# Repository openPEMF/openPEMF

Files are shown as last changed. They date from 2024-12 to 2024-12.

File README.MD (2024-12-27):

# <openPEMF>

## Description

Open source PEMF project that includes the hardware and firmware for anyone looking to build their own PEMF device

- Aren't there already some open source PEMF projects?  
    Yes, but many of them do not create the same fields used in the majority of published PEMF parameters. Most of them also have switching characteristics that cause spurious spike and oscillations that could be considered "dirty electricity"

- Why share this project?  
    Because PEMF with the right parameters has the ability to change peoples lives. From regenerating cartilage to reducing inflammation, many people get out of pain they have had for years. Something this powerful should not be stuck behind high price tags.

- What problem does it solve?  
    PEMF devices with good parameters cost a lot, cheap PEMF devices do not create magnetic fields that use the parameters used in the majority of PEMF studies

This open source PEMF project provides all the files necessary to make your own PEMF device that can be used to re-create the majority of PEMF parameters used in the majority of published PEMF studies.

PEMF has been proven to do lots of amazing things including regenerate cartilage and decrease inflammation, but don't take our word for it, go read some of the published studies and take a look at the science yourself!

The project allows you to tune your own magnetic field intensity and slew rate. This can be accomplished by either changing the voltage from the power supply, or by changing the pulse width.

Reach out with any questions or suggestions! Lets build this together and create a future where all people can access PEMF and benefit from the improved quality of life!
You can reach us at openpemf@gmail.com

## Table of Contents

- [How To Build](#How-to-build)
- [Usage](#usage)
- [Features](#features)

## How to build

The Gerber files, BOM and .POS files are already for purchase at JLCPCB.com. You should be able to upload these to JLCPCB and order complete (or mostly complete - depending on part availability) PCBs ready to run!

Once you have your PCBs, the first thing that you will want to do is upload the arduino code. The file "TEST.ino" is set up to run at 10hz and if you don't want to make any changes you can simply upload this file using the Arduino IDE. You will need to install the Raspberry Pi Pico board definitions since this design uses an RP2040 as it's processor. If you want to re-upload code, there are 2 holes in the pcb that you can bridge with a paperclip to get it into bootloader mode.

If you are not familiar with arduino or PCB ordering we can send out a kit. Email us at openpemf@gmail.com.

This board is designed to fit in this enclosure:
https://www.ebay.com/itm/266629727778?mkcid=16&mkevt=1&mkrid=711-127632-2357-0&ssspo=g7l9ZZJUQN-&sssrc=2047675&ssuid=7-kgmmceqts&widget_ver=artemis&media=COPY

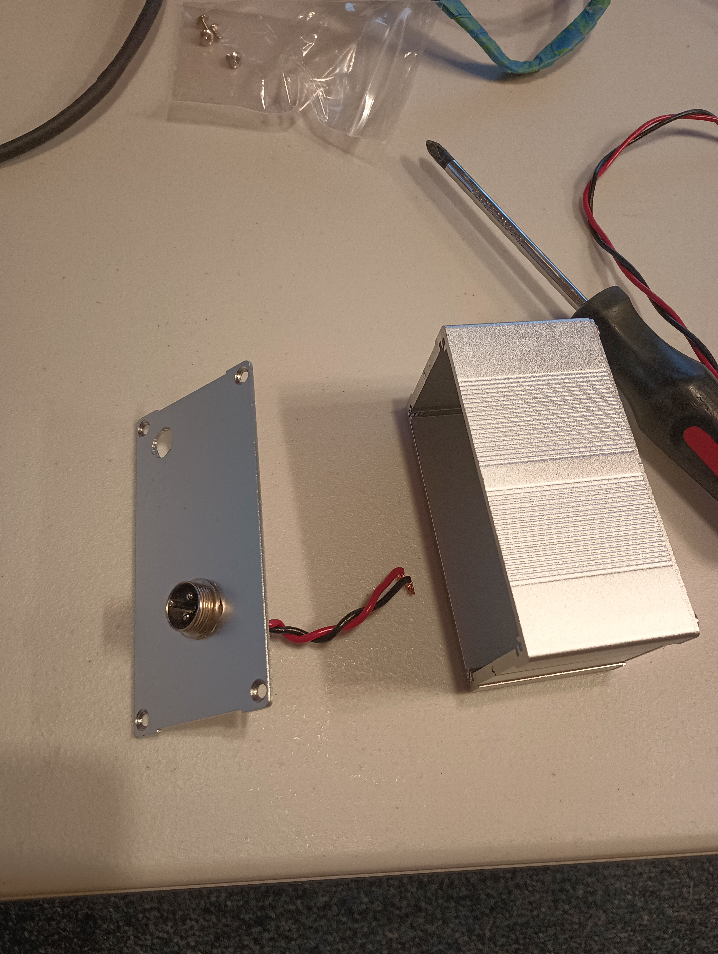
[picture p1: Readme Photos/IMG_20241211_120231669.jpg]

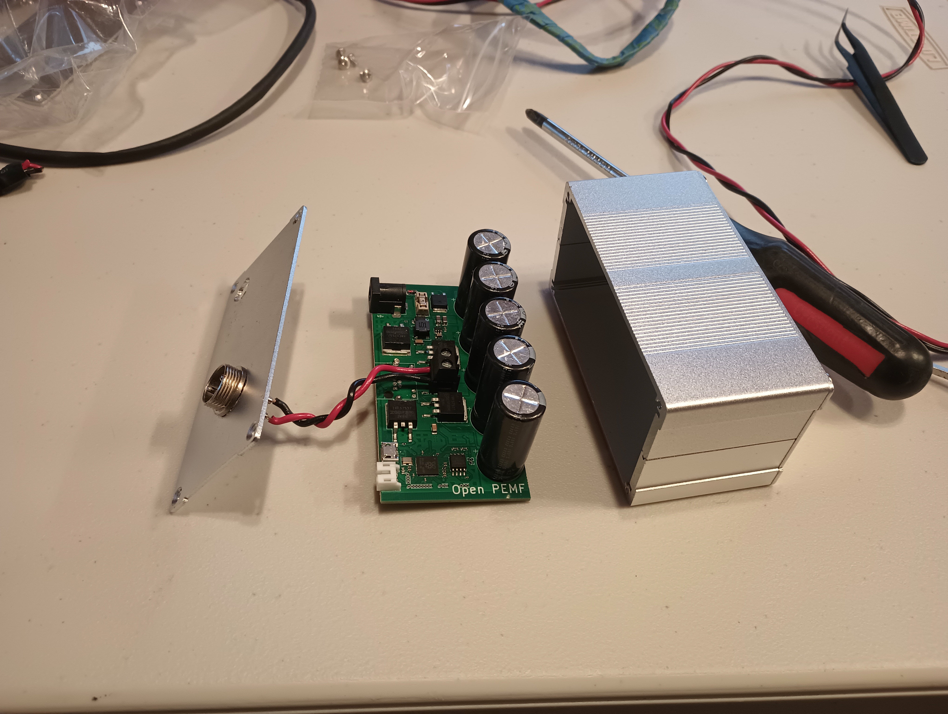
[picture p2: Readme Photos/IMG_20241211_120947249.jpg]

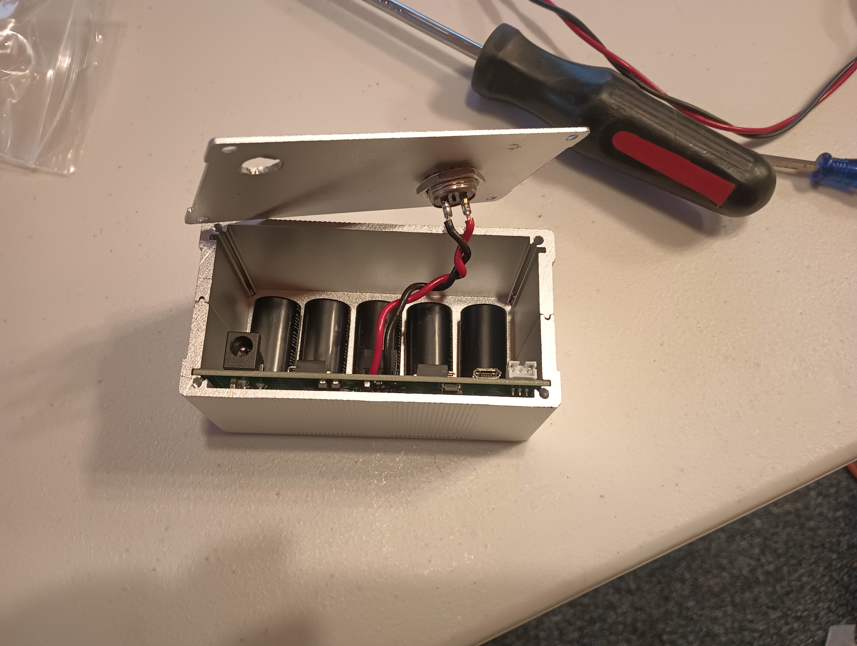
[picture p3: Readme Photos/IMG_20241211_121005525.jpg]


You can see that we used a simple circular connector to get the PEMF power through the enclosure. Ideally a 4 pin connector would be used for larger coils/currents. A handheld drill is an okay option to add the holes. Another option would be something 3D printed or laser cut. Please contribute these if you end up making them!

The coil should be wound from some form of wire. The closer the wires are together, the more efficient the coil will be. Using regular insulated wire still works well, but you will get more magnetic field from using enameled magnet wire.

Here is what our prototype coil looked like:
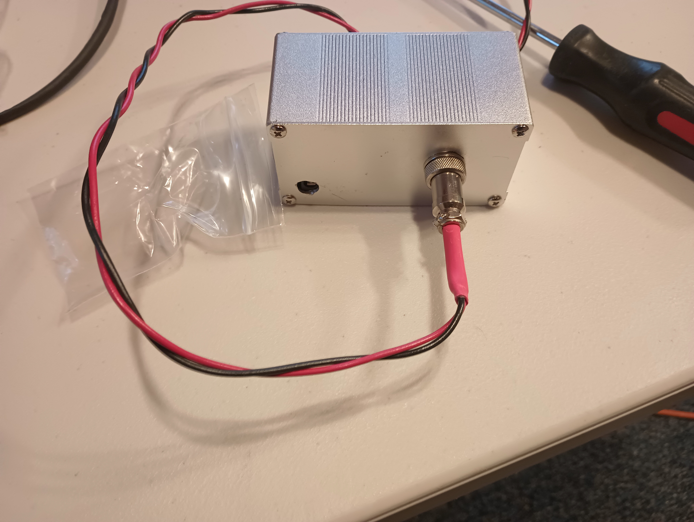
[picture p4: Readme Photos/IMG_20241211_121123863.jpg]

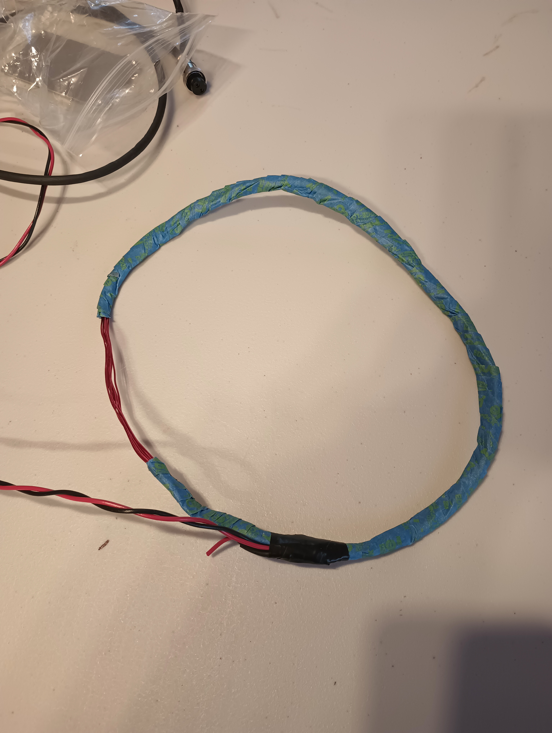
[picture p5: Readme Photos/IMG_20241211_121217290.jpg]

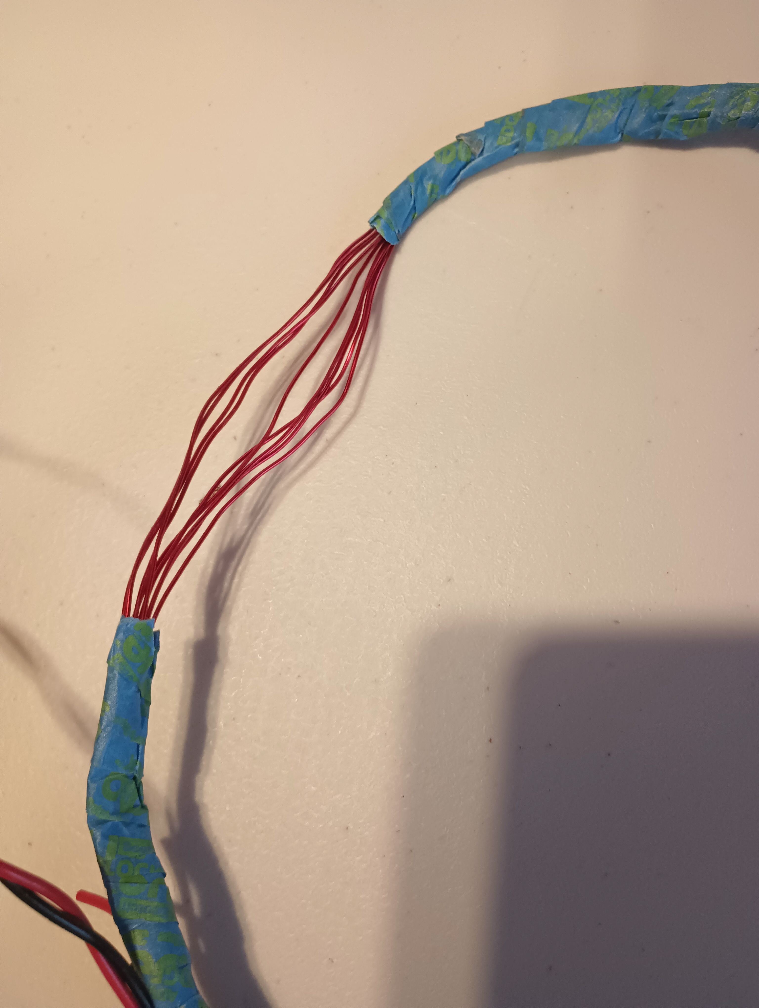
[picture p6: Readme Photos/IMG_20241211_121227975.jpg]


This sensor is great to see what the fields look like around your coil. Simply give it power and connect it to an oscilloscope:
https://www.digikey.com/en/products/detail/asahi-kasei-microdevices-akm/EQ733L/5822654

The coil we made had around 3 mT at the center, and around 10 mT close to the wires.

You will want a power supply that can run the board well. We found that this one worked well:
https://www.digikey.com/en/products/detail/fsp-technology-inc/FSP040-DWAN3/15713237 

## Usage
Simply place the loop over any part of your body that needs improvement. We like to look up published studies to see how long to use the PEMF for. You can even wind coils that are smaller with higher intensity or larger for a larger magnetic field.

## Features

There are a lot of features to OpenPEMF! Here are a few:
* Mosfet gate slew is limited -  this prevents parasitic turn on during the falling side of the signal
* There is an RC snubber across the h-bridge, removing certain oscillations that are not wanted
* Bi-polar pulses
* Programmable frequencies

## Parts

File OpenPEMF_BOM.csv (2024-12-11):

Reference | Value | Footprint | Field5
C1,C4,C5,C11,C12,C14,C34,C39,C40 | 1n_250V | Capacitor_SMD:C_1206_3216Metric | C915351
C2,C3,C15,C16,C17,C18,C19,C20,C21,C22,C23,C24,C25,C35,C36,C41,C42 | 100n | Capacitor_SMD:C_0402_1005Metric | C307331
C6,C26,C28,C29,C43,C44 | 2.2u | Capacitor_SMD:C_1206_3216Metric | C577211
C7,C8,C9,C10,C13 | 470u_100V | Capacitor_THT:CP_Radial_D16.0mm_P7.50mm | C340709
C27,C30,C31,C32,C37,C38 | 4.7u | Capacitor_SMD:C_1206_3216Metric | C29823
C33 | 100n | Capacitor_SMD:C_0805_2012Metric | C28233
C45,C46 | 36pf | Capacitor_SMD:C_0402_1005Metric | C541436
D1,D2,D16,D17,D21,D22 | BAT46W-7-F | Diode_SMD:D_SOD-123 | C83152
D3,D4,D14,D15,D18,D19 | 5.6 | Diode_SMD:D_MiniMELF | C2982194
D5,D6,D7,D23 | D_AAK | Package_TO_SOT_SMD:TO-277A | C2693410
D8 | SMAJ54CA | Diode_SMD:D_SMA | C173507
D20 | D_Schottky | Diode_SMD:D_SMA | C14996
F1 | 0154005.DRT | Fuse:Fuseholder_Littelfuse_Nano2_154x | C206917
J2 | Screw_Terminal_01x02 | TerminalBlock_Phoenix:TerminalBlock_Phoenix_MKDS-1,5-2-5.08_1x02_P5.08mm_Horizontal | C430601
J3,J4,J5,J7,J9 | -- mixed values -- | -- mixed values --
J8 | USB_B_Micro | OpenPEMFfp:AMPHENOL_10118194-0001LF | C132563
J10 | Barrel_Jack_Switch | OpenPEMFfp:C319099 | C720558
L1 | 100u | Inductor_SMD:L_Coilcraft_XAL6060-XXX | C341070
Q1,Q2,Q3,Q4 | Q_NMOS_GDS | Package_TO_SOT_SMD:TO-263-2 | C538034
Q5 | Q_PMOS_GDS | Package_TO_SOT_SMD:TO-252-2 | C2585
R1,R2,R7,R8,R14,R18 | 1k | Resistor_SMD:R_0603_1608Metric | C21190
R3,R12,R13 | 150 | Resistor_SMD:R_0805_2012Metric | C17471
R4,R11,R25 | 100 | Resistor_SMD:R_0402_1005Metric | C25076
R5,R9,R15,R16 | 27.4 | Resistor_SMD:R_0402_1005Metric | C172043
R6,R10,R19,R23 | 100k | Capacitor_SMD:C_0603_1608Metric | C25803
R17,R21,R22 | 10k | Resistor_SMD:R_0603_1608Metric | C25804
R20 | 1Meg | Capacitor_SMD:C_0603_1608Metric | C22935
R24 | 6.8k | Resistor_SMD:R_0603_1608Metric | C23212
U2 | TL072 | Package_SO:SOIC-8_3.9x4.9mm_P1.27mm | C6961
U3,U5 | EL3H7BTA-VG | OpenPEMFfp:SOIC_BTA-VG_EVS | C32565
U6 | RP2040 | OpenPEMFfp:RP2040 | C2040
U7 | W25Q128JVS | Package_SO:SOIC-8_5.23x5.23mm_P1.27mm | C97521
U8 | AMS1117-3.3 | Package_TO_SOT_SMD:SOT-223-3_TabPin2 | C6186
U9 | LMR16006 | Package_TO_SOT_SMD:SOT-23-6 | C87080
U10 | NE555DR | Package_SO:SOIC-8_3.9x4.9mm_P1.27mm | C7593
Y1 | 12Mhz | Crystal:Crystal_SMD_3225-4Pin_3.2x2.5mm | C9002

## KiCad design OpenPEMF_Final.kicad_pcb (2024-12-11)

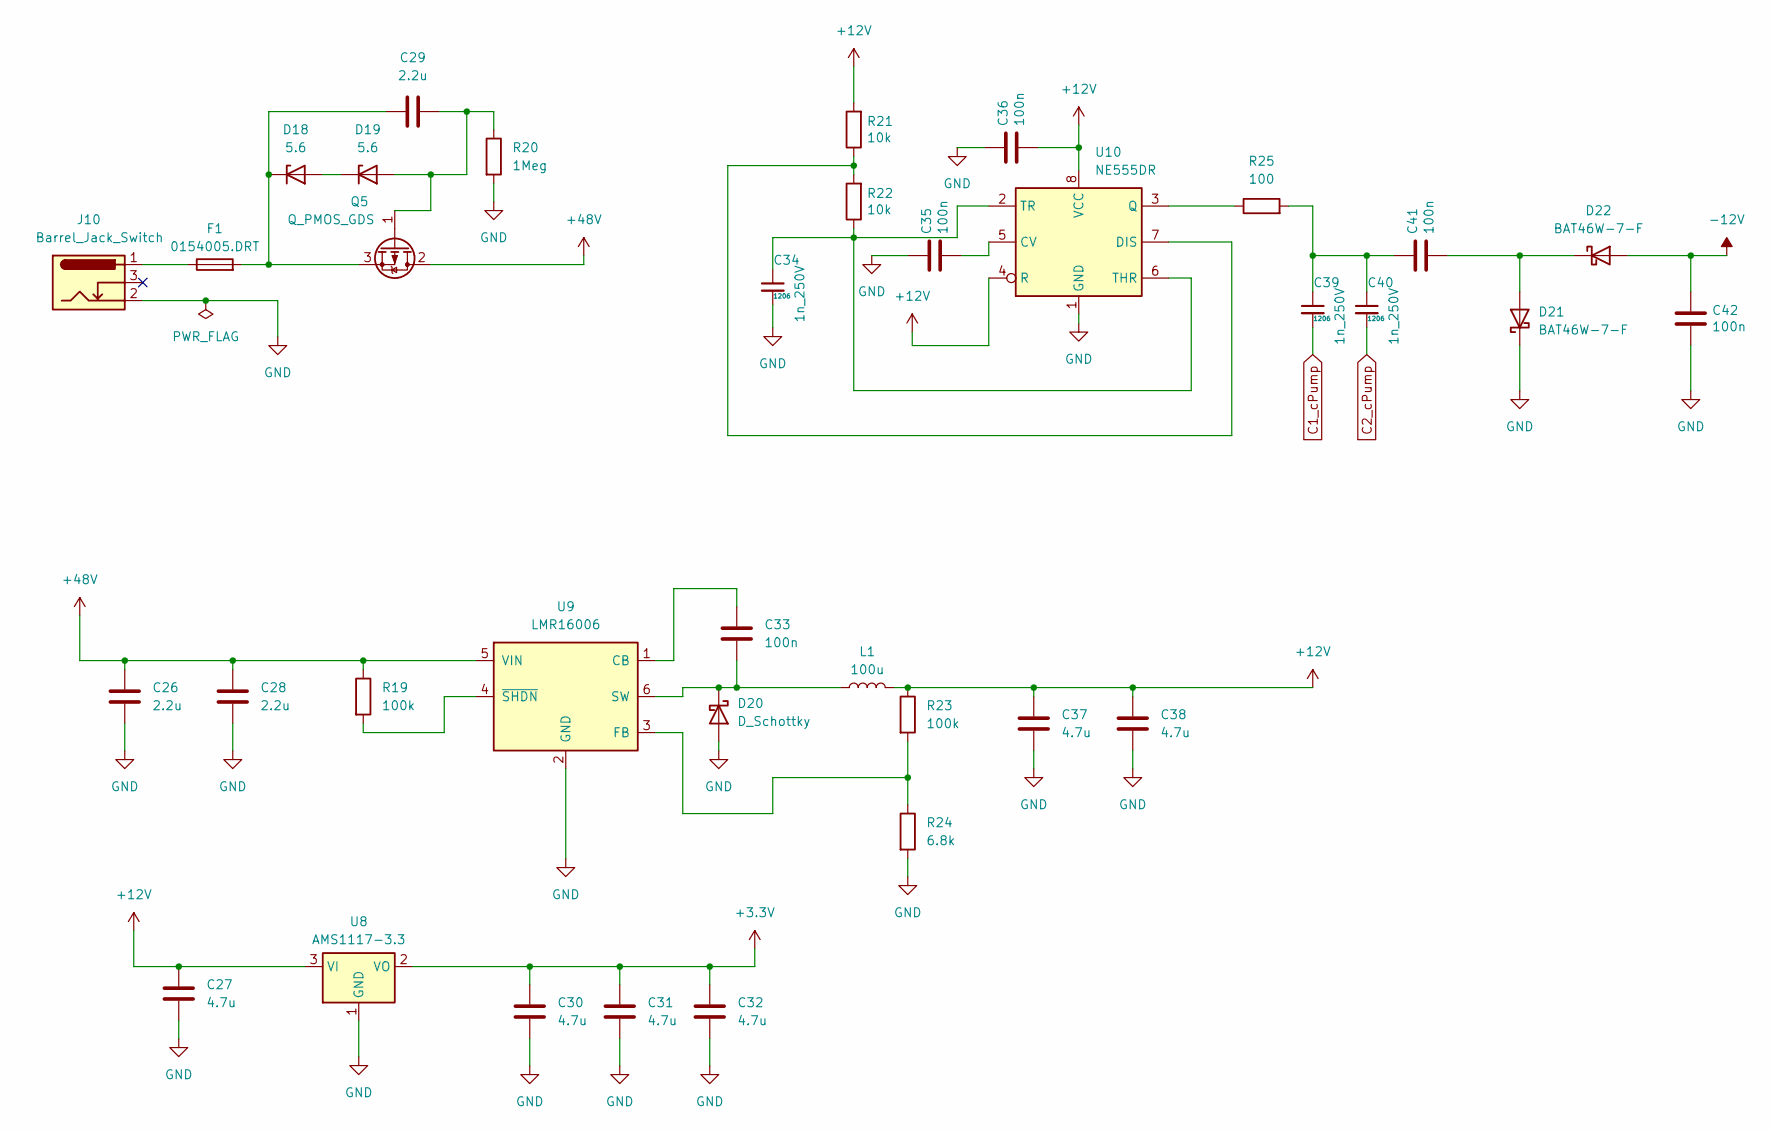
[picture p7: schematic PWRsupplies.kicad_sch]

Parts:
C26, C28, C29: 2.2u; C_1206_3216Metric
C27, C30, C31, C32, C37, C38: 4.7u; C_1206_3216Metric
C33: 100n; C_0805_2012Metric
C34, C39, C40: 1n_250V; C_1206_3216Metric
C35, C36, C41, C42: 100n; C_0402_1005Metric
D18, D19: 5.6; D_MiniMELF
D20: D_Schottky; D_SMA
D21, D22: BAT46W-7-F; D_SOD-123
F1: 0154005.DRT; Fuseholder_Littelfuse_Nano2_154x
J10: Barrel_Jack_Switch; C319099
L1: 100u; L_Coilcraft_XAL6060-XXX
Q5: Q_PMOS_GDS; TO-252-2
R19, R23: 100k; C_0603_1608Metric
R20: 1Meg; C_0603_1608Metric
R21, R22: 10k; R_0603_1608Metric
R24: 6.8k; R_0603_1608Metric
R25: 100; R_0402_1005Metric
U8: AMS1117-3.3; SOT-223-3_TabPin2
U9: LMR16006; SOT-23-6
U10: NE555DR; SOIC-8_3.9x4.9mm_P1.27mm

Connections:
+3.3V: C30.1, C31.1, C32.1, U8.2 (VO); also elsewhere on the board
+12V: C27.1, C36.2, C37.1, C38.1, L1.2, R21.2, R23.1, U8.3 (VI), U10.4 (R), U10.8 (VCC); also elsewhere on the board
+48V: C26.1, C28.1, Q5.2 (D), R19.1, U9.5 (VIN); also elsewhere on the board
-12V: C42.1, D22.2 (A); also elsewhere on the board
C1_cPump: C39.2; also elsewhere on the board
C2_cPump: C40.2; also elsewhere on the board
GND: C26.2, C27.2, C28.2, C30.2, C31.2, C32.2, C34.2, C35.1, C36.1, C37.2, C38.2, C42.2, D20.2 (A), D21.1 (K), J10.2, R20.2, R24.2, U8.1 (GND), U9.2 (GND), U10.1 (GND); also elsewhere on the board
unnamed: C39.1, C40.1, C41.1, R25.2
unnamed: D18.2 (A), D19.1 (K)
unnamed: C29.1, D18.1 (K), F1.2, Q5.3 (S)
unnamed: C29.2, D19.2 (A), Q5.1 (G), R20.1
unnamed: C33.2, D20.1 (K), L1.1, U9.6 (SW)
unnamed: C41.2, D21.2 (A), D22.1 (K)
unnamed: F1.1, J10.1
unnamed: C33.1, U9.1 (CB)
unnamed: R23.2, R24.1, U9.3 (FB)
unnamed: R19.2, U9.4 (~SHDN)
unnamed: C35.2, U10.5 (CV)
unnamed: R21.1, R22.2, U10.7 (DIS)
unnamed: R25.1, U10.3 (Q)
unnamed: C34.1, R22.1, U10.2 (TR), U10.6 (THR)

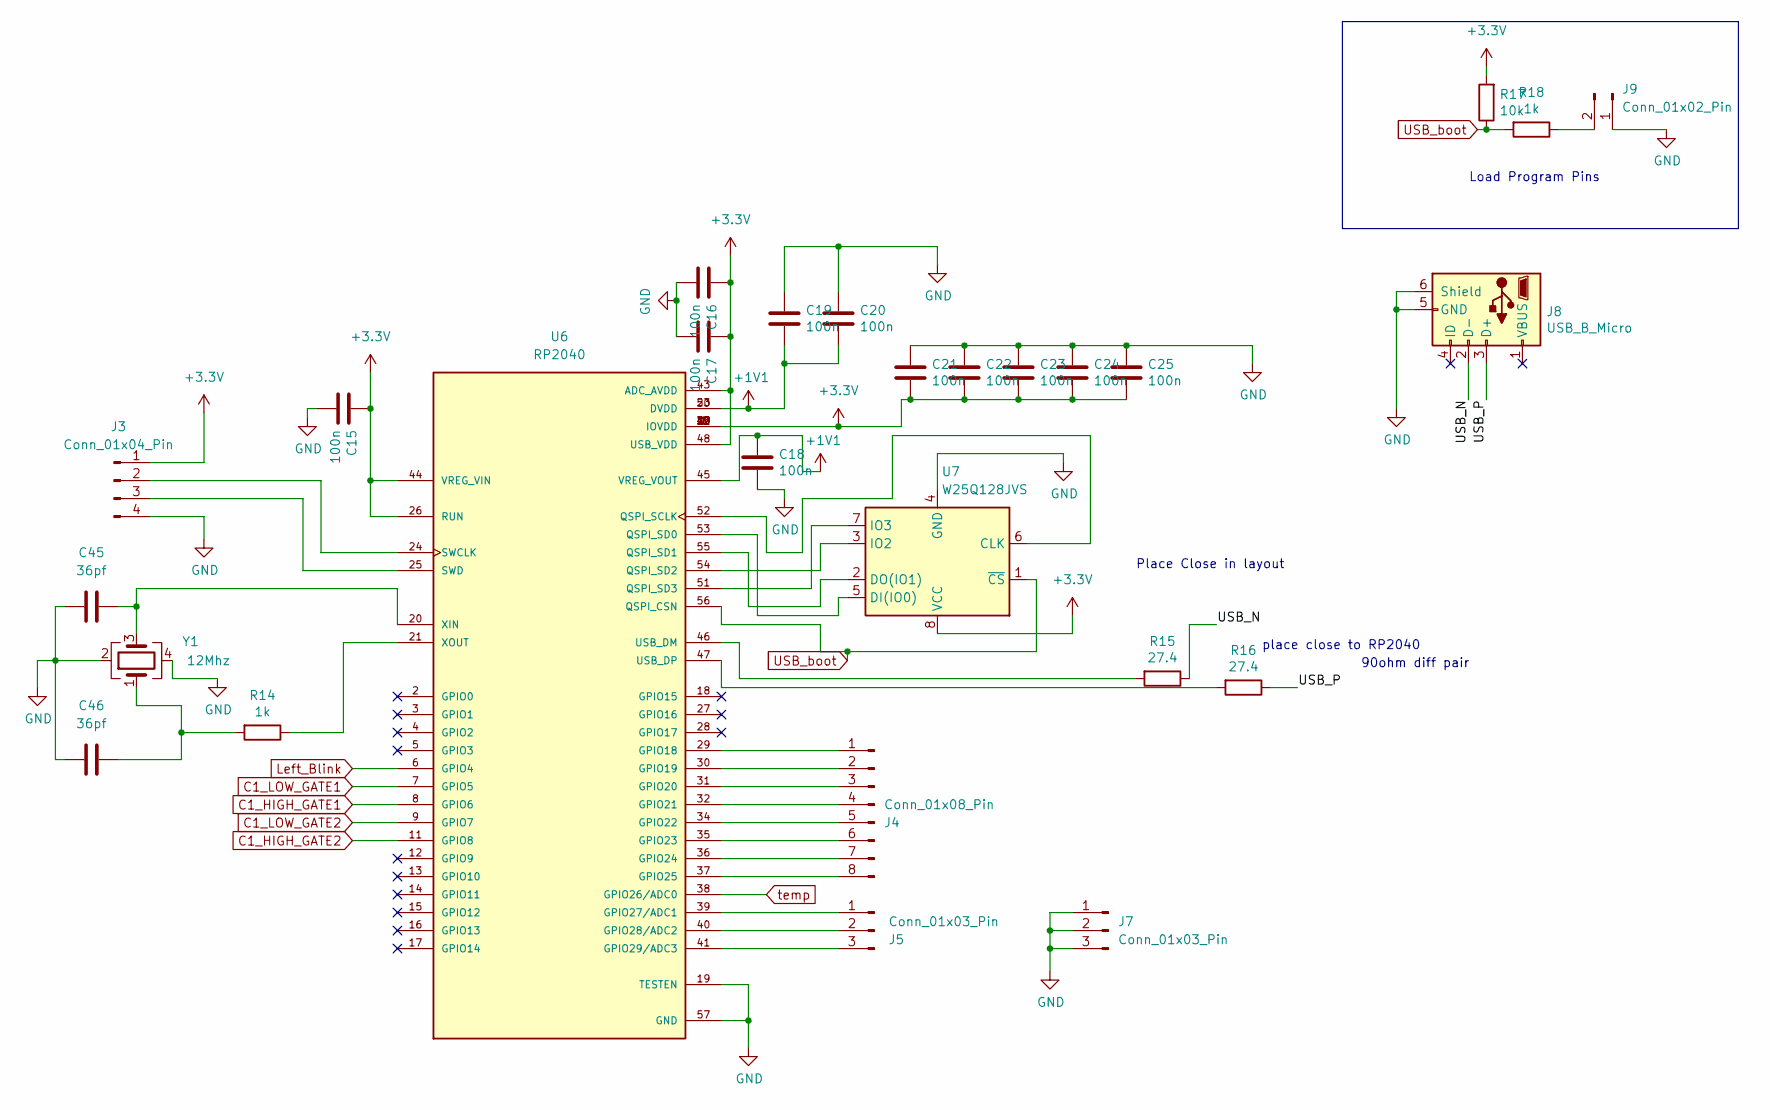
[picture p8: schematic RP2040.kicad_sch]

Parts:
C15, C16, C17, C18, C19, C20, C21, C22, C23, C24, C25: 100n; C_0402_1005Metric
C45, C46: 36pf; C_0402_1005Metric
J3: Conn_01x04_Pin; PinHeader_1x04_P1.00mm_Vertical
J4: Conn_01x08_Pin; PinHeader_1x08_P1.00mm_Vertical
J5, J7: Conn_01x03_Pin; PinHeader_1x03_P1.00mm_Vertical
J8: USB_B_Micro; AMPHENOL_10118194-0001LF
J9: Conn_01x02_Pin; PinHeader_1x02_P1.27mm_Vertical
R14, R18: 1k; R_0603_1608Metric
R15, R16: 27.4; R_0402_1005Metric
R17: 10k; R_0603_1608Metric
U6: RP2040; PARTREV 1.6.1
U7: W25Q128JVS; SOIC-8_5.23x5.23mm_P1.27mm
Y1: 12Mhz; Crystal_SMD_3225-4Pin_3.2x2.5mm

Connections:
+1V1: C18.1, C19.2, C20.2, U6.23 (DVDD), U6.45 (VREG_VOUT), U6.50 (DVDD)
+3.3V: C15.1, C16.1, C17.1, C21.2, C22.2, C23.2, C24.2, C25.2, J3.1, R17.2, U6.1 (IOVDD), U6.10 (IOVDD), U6.22 (IOVDD), U6.26 (RUN), U6.33 (IOVDD), U6.42 (IOVDD), U6.43 (ADC_AVDD), U6.44 (VREG_VIN), U6.48 (USB_VDD), U6.49 (IOVDD), U7.8 (VCC); also elsewhere on the board
/RP2040/USB_N: J8.2 (D-), R15.1
/RP2040/USB_P: J8.3 (D+), R16.1
C1_HIGH_GATE1: U6.8 (GPIO6); also elsewhere on the board
C1_HIGH_GATE2: U6.11 (GPIO8); also elsewhere on the board
C1_LOW_GATE1: U6.7 (GPIO5); also elsewhere on the board
C1_LOW_GATE2: U6.9 (GPIO7); also elsewhere on the board
GND: C15.2, C16.2, C17.2, C18.2, C19.1, C20.1, C21.1, C22.1, C23.1, C24.1, C25.1, C45.2, C46.2, J3.4, J7.1, J7.2, J7.3, J8.5 (GND), J8.6 (Shield), J9.1, U6.19 (TESTEN), U6.57 (GND), U7.4 (GND), Y1.2, Y1.4; also elsewhere on the board
Left_Blink: U6.6 (GPIO4)
unnamed: C46.1, R14.2, Y1.1
unnamed: J3.2, U6.24 (SWCLK)
unnamed: J3.3, U6.25 (SWD)
unnamed: J4.1, U6.29 (GPIO18)
unnamed: J4.2, U6.30 (GPIO19)
unnamed: J4.3, U6.31 (GPIO20)
unnamed: J4.4, U6.32 (GPIO21)
unnamed: J4.5, U6.34 (GPIO22)
unnamed: J4.6, U6.35 (GPIO23)
unnamed: J4.7, U6.36 (GPIO24)
unnamed: J4.8, U6.37 (GPIO25)
unnamed: J5.1, U6.39 (GPIO27/ADC1)
unnamed: J5.2, U6.40 (GPIO28/ADC2)
unnamed: J5.3, U6.41 (GPIO29/ADC3)
unnamed: J9.2, R18.1
unnamed: U6.52 (QSPI_SCLK), U7.6 (CLK)
unnamed: U6.53 (QSPI_SD0), U7.5 (DI(IO0))
unnamed: U6.55 (QSPI_SD1), U7.2 (DO(IO1))
unnamed: U6.54 (QSPI_SD2), U7.3 (IO2)
unnamed: U6.51 (QSPI_SD3), U7.7 (IO3)
unnamed: R15.2, U6.46 (USB_DM)
unnamed: R16.2, U6.47 (USB_DP)
unnamed: C45.1, U6.20 (XIN), Y1.3
unnamed: R14.1, U6.21 (XOUT)
USB_boot: R17.1, R18.2, U6.56 (QSPI_CSN), U7.1 (~CS)
temp: U6.38 (GPIO26/ADC0)

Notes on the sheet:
Load Program Pins
Place Close in layout
place close to RP2040
90ohm diff pair

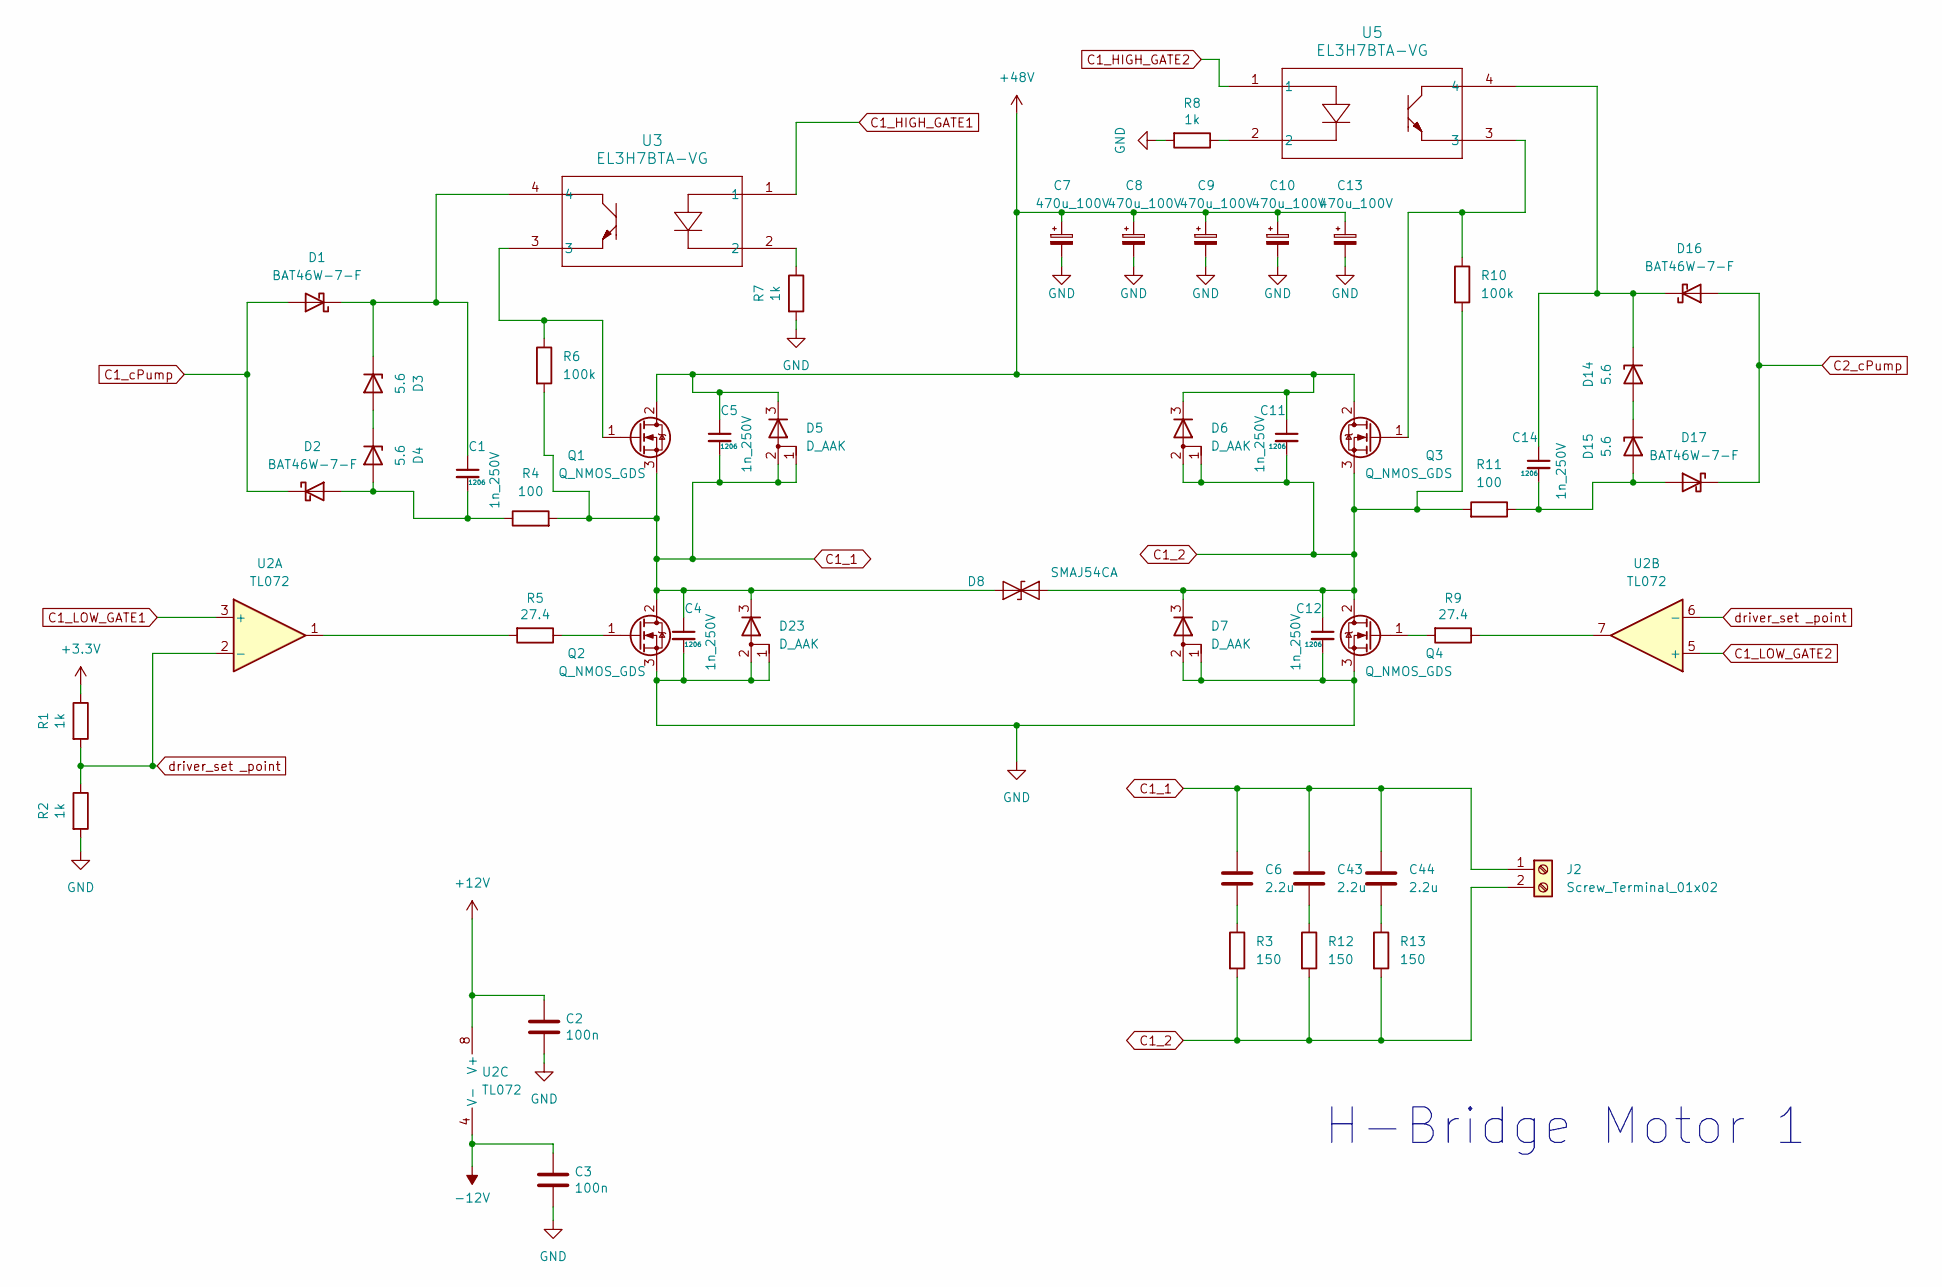
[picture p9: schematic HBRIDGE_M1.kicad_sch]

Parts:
C1, C4, C5, C11, C12, C14: 1n_250V; C_1206_3216Metric
C2, C3: 100n; C_0402_1005Metric
C6, C43, C44: 2.2u; C_1206_3216Metric
C7, C8, C9, C10, C13: 470u_100V; CP_Radial_D16.0mm_P7.50mm
D1, D2, D16, D17: BAT46W-7-F; D_SOD-123
D3, D4, D14, D15: 5.6; D_MiniMELF
D5, D6, D7, D23: D_AAK; TO-277A
D8: SMAJ54CA; D_SMA
J2: Screw_Terminal_01x02; TerminalBlock_Phoenix_MKDS-1,5-2-5.08_1x02_P5.08mm_Horizont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
Q1, Q2, Q3, Q4: Q_NMOS_GDS; TO-263-2
R1, R2, R7, R8: 1k; R_0603_1608Metric
R3, R12, R13: 150; R_0805_2012Metric
R4, R11: 100; R_0402_1005Metric
R5, R9: 27.4; R_0402_1005Metric
R6, R10: 100k; C_0603_1608Metric
U2: TL072; SOIC-8_3.9x4.9mm_P1.27mm
U3, U5: EL3H7BTA-VG; SOIC_BTA-VG_EVS

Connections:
+3.3V: R1.1; also elsewhere on the board
+12V: C2.1, U2.8 (V+); also elsewhere on the board
+48V: C5.1, C7.1, C8.1, C9.1, C10.1, C11.1, C13.1, D5.3 (K), D6.3 (K), Q1.2 (D), Q3.2 (D); also elsewhere on the board
-12V: C3.1, U2.4 (V-); also elsewhere on the board
C1_1: C4.1, C5.2, C6.1, C43.1, C44.1, D5.1 (A), D5.2 (A), D8.2 (A2), D23.3 (K), J2.1, Q1.3 (S), Q2.2 (D), R4.2, R6.2
C1_2: C11.2, C12.1, D6.1 (A), D6.2 (A), D7.3 (K), D8.1 (A1), J2.2, Q3.3 (S), Q4.2 (D), R3.2, R10.2, R11.2, R12.2, R13.2
C1_HIGH_GATE1: U3.1; also elsewhere on the board
C1_HIGH_GATE2: U5.1; also elsewhere on the board
C1_LOW_GATE1: U2.3 (+); also elsewhere on the board
C1_LOW_GATE2: U2.5 (+); also elsewhere on the board
C1_cPump: D1.2 (A), D2.1 (K); also elsewhere on the board
C2_cPump: D16.2 (A), D17.1 (K); also elsewhere on the board
GND: C2.2, C3.2, C4.2, C7.2, C8.2, C9.2, C10.2, C12.2, C13.2, D7.1 (A), D7.2 (A), D23.1 (A), D23.2 (A), Q2.3 (S), Q4.3 (S), R2.2, R7.2, R8.2; also elsewhere on the board
unnamed: C6.2, R3.1
unnamed: C43.2, R12.1
unnamed: C44.2, R13.1
unnamed: C1.1, D1.1 (K), D3.1 (K), U3.4
unnamed: C1.2, D2.2 (A), D4.2 (A), R4.1
unnamed: D3.2 (A), D4.1 (K)
unnamed: D14.2 (A), D15.1 (K)
unnamed: C14.1, D14.1 (K), D16.1 (K), U5.4
unnamed: C14.2, D15.2 (A), D17.2 (A), R11.1
unnamed: Q1.1 (G), R6.1, U3.3
unnamed: Q2.1 (G), R5.1
unnamed: Q3.1 (G), R10.1, U5.3
unnamed: Q4.1 (G), R9.2
unnamed: R5.2, U2.1
unnamed: R7.1, U3.2
unnamed: R8.1, U5.2
unnamed: R9.1, U2.7
driver_set _point: R1.2, R2.1, U2.2 (-), U2.6 (-)

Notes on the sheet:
H-Bridge Motor 1

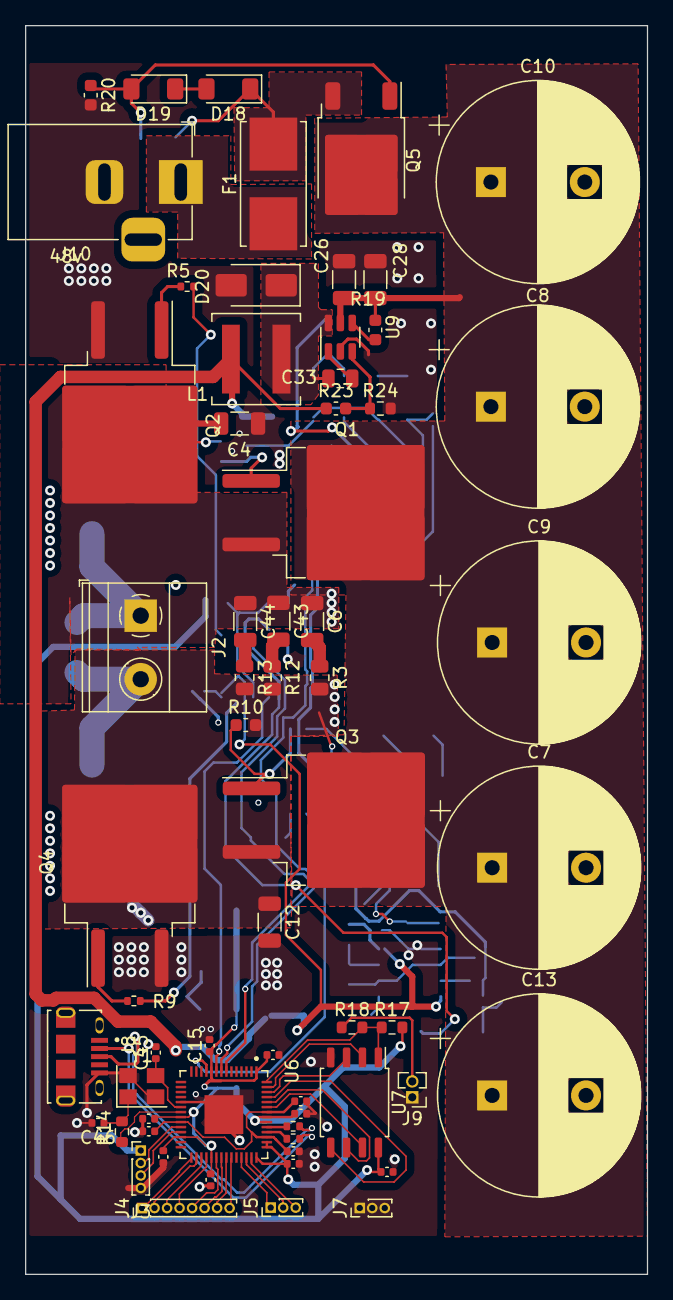
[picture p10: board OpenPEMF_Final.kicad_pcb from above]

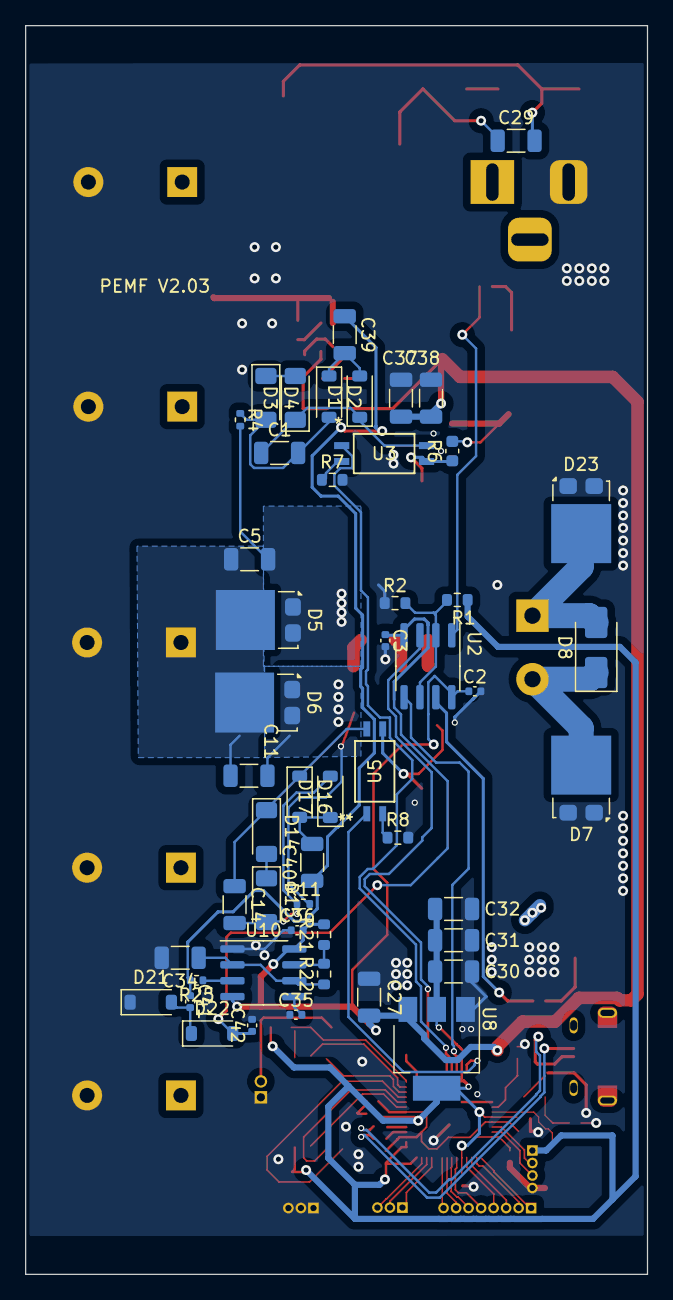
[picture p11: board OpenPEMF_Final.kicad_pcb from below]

Board: 4 copper layers, 49.7 x 99.8 mm, 113 parts (50 on the bottom side), 73 nets.

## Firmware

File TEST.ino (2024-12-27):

void setup() {
  // put your setup code here, to run once:
  pinMode(4, OUTPUT);
  pinMode(5, OUTPUT);
  pinMode(6, OUTPUT);
  pinMode(7, OUTPUT);
  pinMode(8, OUTPUT);
  delay(1250);
}
unsigned long lastPulse;
bool polarity = 0;

void loop() {
  // put your main code here, to run repeatedly:

  if (millis() - lastPulse > 100)
  {
    if (polarity)
    {
      digitalWrite(8, LOW);
      digitalWrite(6, HIGH);
      lastPulse = millis();
      digitalWrite(7, HIGH);
      delayMicroseconds(100);
      digitalWrite(7, LOW);
      polarity = 0;
    }
    else {
      digitalWrite(6, LOW);
      digitalWrite(8, HIGH);
      lastPulse = millis();
      digitalWrite(5, HIGH);
      delayMicroseconds(100);
      digitalWrite(5, LOW);
      polarity = 1;
    }
  }
  if (millis() - lastPulse > 15)
  {
    if (polarity)
    {
      digitalWrite(8, LOW);
      digitalWrite(6, HIGH);
    }
    else {
      digitalWrite(6, LOW);
      digitalWrite(8, HIGH);
    }

  }
  digitalWrite(4,polarity);

}
